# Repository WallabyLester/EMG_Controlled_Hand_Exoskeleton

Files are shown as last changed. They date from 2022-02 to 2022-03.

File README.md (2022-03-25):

# EMG Controlled Hand Exoskeleton

https://user-images.githubusercontent.com/90433630/159782526-b3bb951d-2681-48af-9a75-46fd34234eaf.mp4
<p>Playing You Are My Sunshine</p>

## Overview
The goal of this project was to design an EMG controlled hand exoskeleton that would aid stroke patients in playing the piano. The exoskeleton is 3D printed with the `.stl` and `.step` files located in the `cad` directory. You can view individual `.stl` files to see what the parts look like prior to printing. Parts were printed on a Ultimaker 3 with black tough PLA. Most connections are press fit or printed, but four screws and nuts are needed to connect the metacarpal to the hand_dorsal (washers can be added if the screw/nut pair is not big enough). Refer to `cad/exoskeleton.png` for an image of what the completed exoskeleton looks like. 

Four Pololu HP 6V 298:1 Micro Metal Gearmotors were used for the joints and are housed in the finger joint. 12 CPR, 2.7-18V Magnetic Encoders from Pololu were used for each motor. MyoWare Muscle Sensors were used to acquire the EMG signals. 

The microcontroller for this project was an Arduino Uno; used for speed of prototyping, but can be upgraded to any controller if equivalent motor drivers are added. The motor driver in this case was the Adafruit Motor Shield as it allowed direct interfacing with the Arduino and control of four DC motors. 

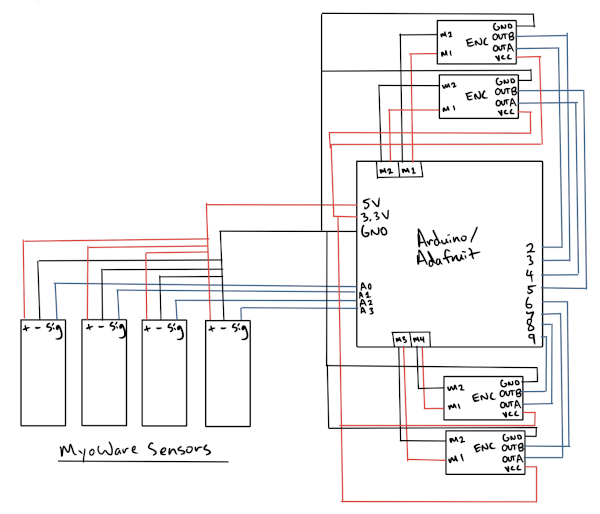
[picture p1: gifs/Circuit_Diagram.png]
Circuit Diagram


There are three available control modes:
1. Using thresholds. Thresholding uses manually found thresholds from EMG readings and basic motor control in which the fingers move up and down a set amount based on an input power. 

2. Using machine learning (ML) classification. ML classification uses the contained ML models to predict which finger is being moved and moves the associated motor with basic motor control based on an input power.

3. Using ML classification with encoder position control from a PID feedback loop. ML classification with the encoders implements external and internal interrupts to read encoder values and perform position control using a PID feedback loop. The Arduino Uno only has two interrupt pins (2 and 3) so an internal interrupt was made using Timer1 (16 bit). 

The control signal is provided by Myoware EMG sensors which provide a processed EMG signal. The signals are amplified, rectified, and integrated before being output. The sensors also offer a raw EMG signal if you would like to perform your own processing. Code for reading from the EMG sensors, saving readings, and plotting data are in the `code` directory. 

Machine learning is used on the EMG readings received from four sensor readings, enabling classification of the signals in 5 modes: 0 - no flexion, 1 - index finger flexed, 2 - middle finger flexed, 3 - fourth finger flexed, and 4 - pinky finger flexed. `Classification_Notes` contains the various scikit-learn machine learning models as well as a Tensorflow model. Refer to it for further notes on the models and GridSearchCV to find the best hyperparameters for the models. The trained models have been saved serialized in the `Trained_models` directory.

There are four available models: 

1. K Nearest Neighbors - KNN predicts the class by calculating the distance between the input point and all of the other points. The algorithm then selects the K number of points which is closest to the input point and uses a majority vote for which class this input must be in. 

2. Random forest classifier - RFC is made up of many decision trees. It builds an uncorrelated forest of trees which can provide a more accurate prediction than just one tree. Decision trees predict an input class based on decision rules which causes branches from each "node". 

3. Multilayer perceptron - MLP is a feed forward neural network. It uses an input layer, output layer, and any number of hidden layers. With an increased number of hidden layers it is able to predict more complex classes. They can also solved non-linear classification problems.

## Usage Instructions
Compile `EMGControlEncoder.ino` onto the Arduino and run `Send_Mode.py` in a terminal with `python3 Send_Mode.py` to start predicting EMG readings. The code will print out the predicted mode. 

Use `EMGControl.ino` for running ML classification with basic motor control and `EMGControlThresholds.ino` to run basic motor control using thresholds. 

Use `EMGControlTest.ino` if you would like to test individual EMG sensor and motor control.

Use `EMGToSerial.ino` to output the EMG readings as serial data and run `Read_EMG_Data.py` to save the data. Run `Plotting.py` to plot individual data file EMG readings and modes.

Use `EncoderRead.ino` to read all the encoders and `EncoderPosition.ino` to control motor movements using all the encoders. 

Use `MotorControl.ino` to test movement of individual motors and `Stop.ino` to stop all motor movement if you are running things and would like to halt them.

## Configuration Instructions
The classification model used in `Send_Mode.py` can be changed based on which ML model you would like to use. Change the line: `filename` to use different models.

The encoder positions can be adjusted based on the desired amount to move the fingers. These would be the `pos_index`, `pos_middle`, `pos_fourth`, and `pos_pinky` variables in the encoder control files.

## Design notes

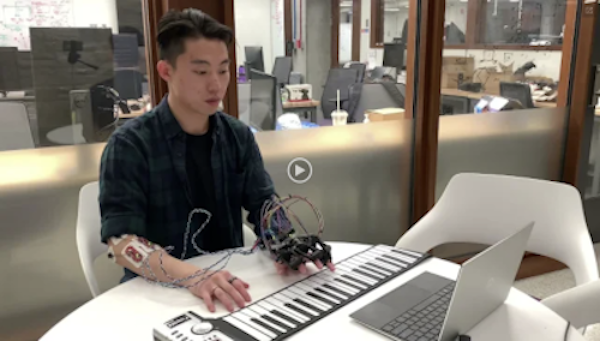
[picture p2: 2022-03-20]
gifs/Final_Demo.png

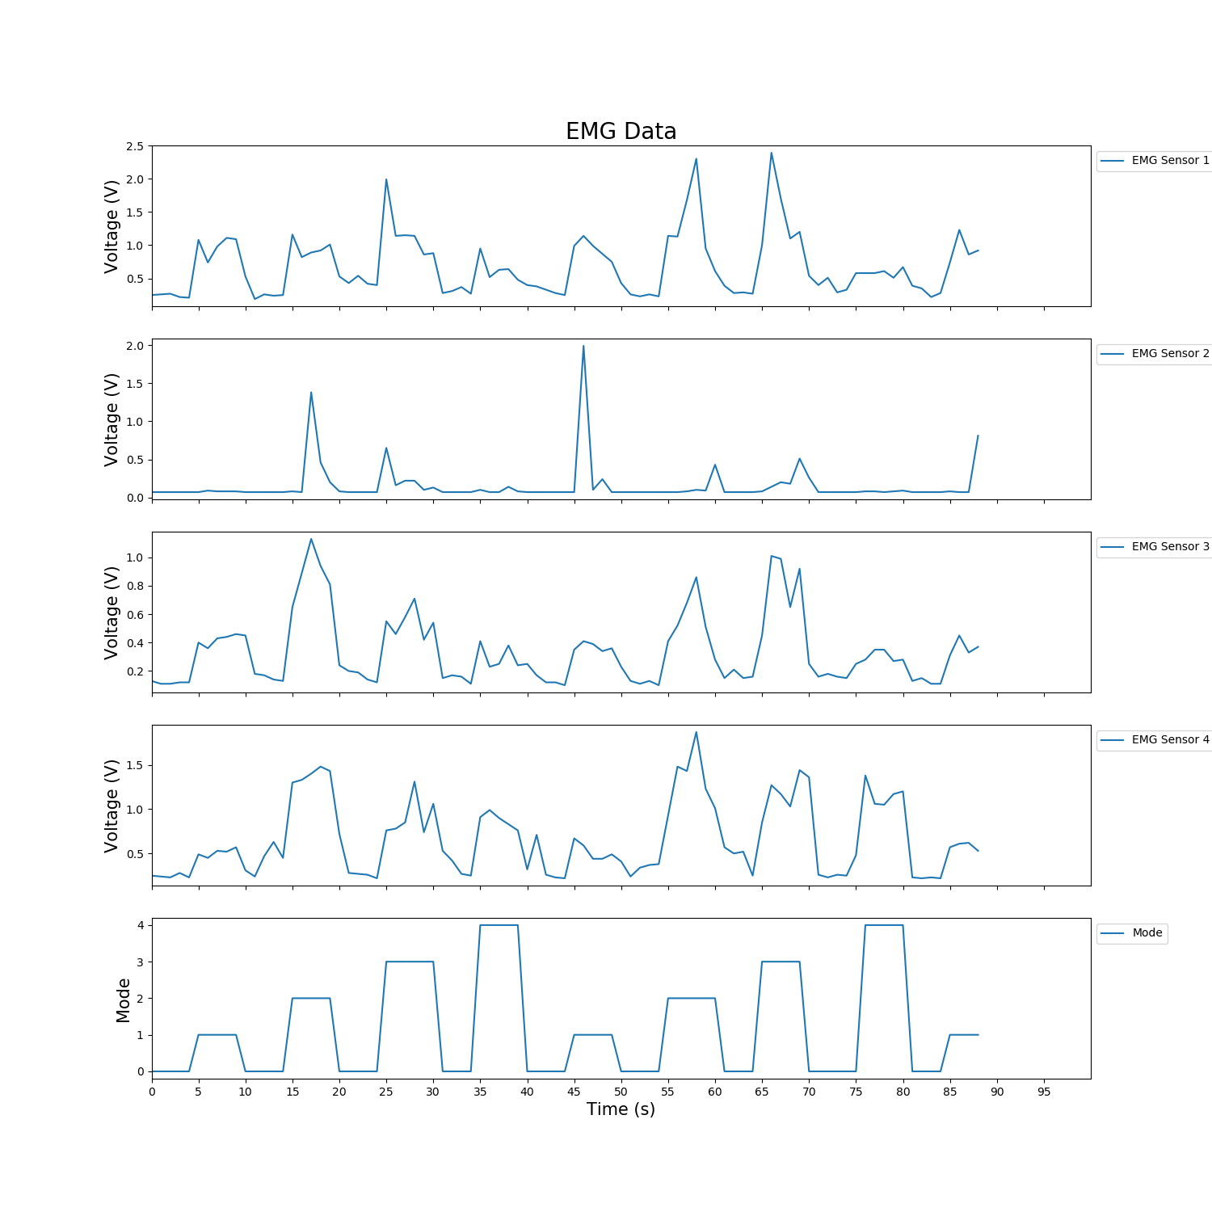
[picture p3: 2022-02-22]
code/plots/Combined_EMG_data5.png

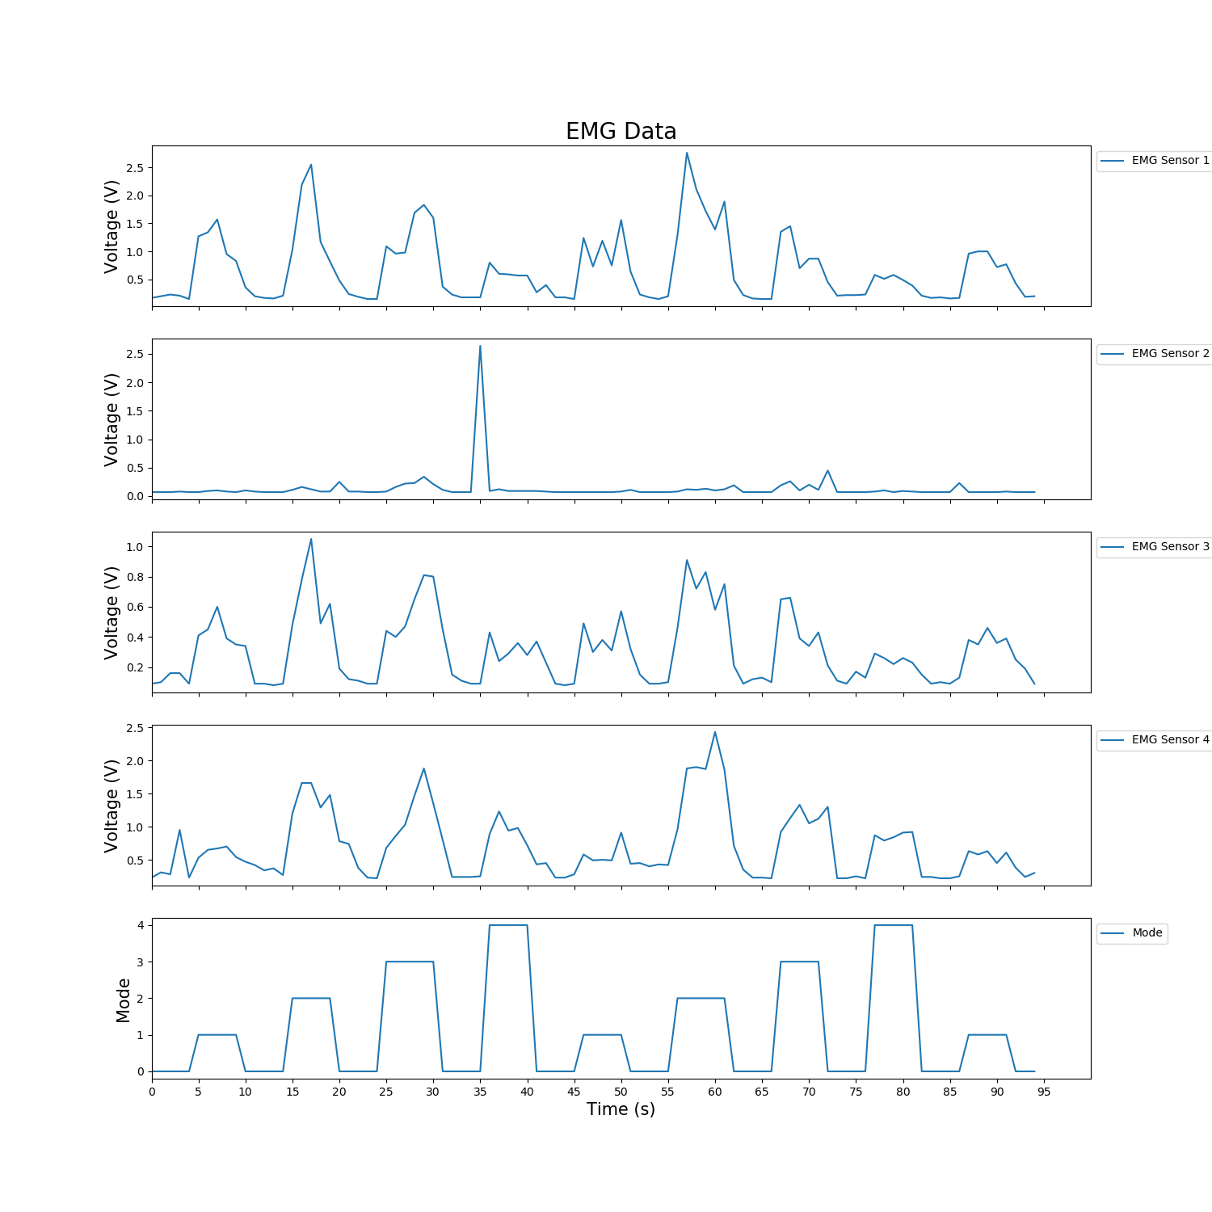
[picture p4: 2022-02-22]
code/plots/Combined_EMG_data8.png

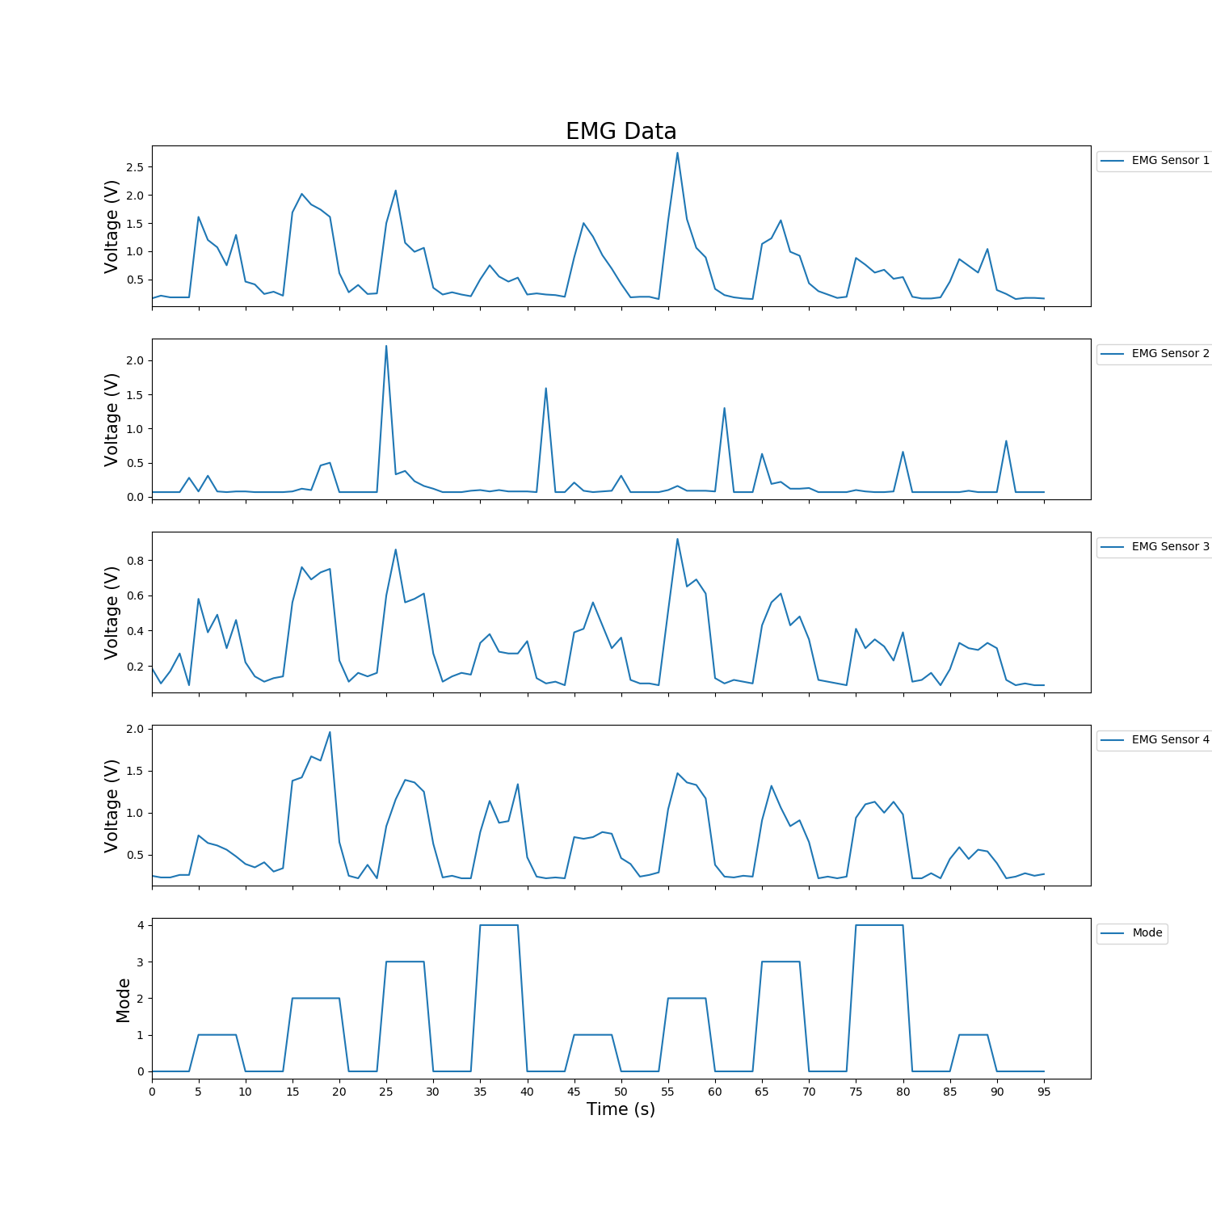
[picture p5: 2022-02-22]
code/plots/Combined_EMG_data10.png

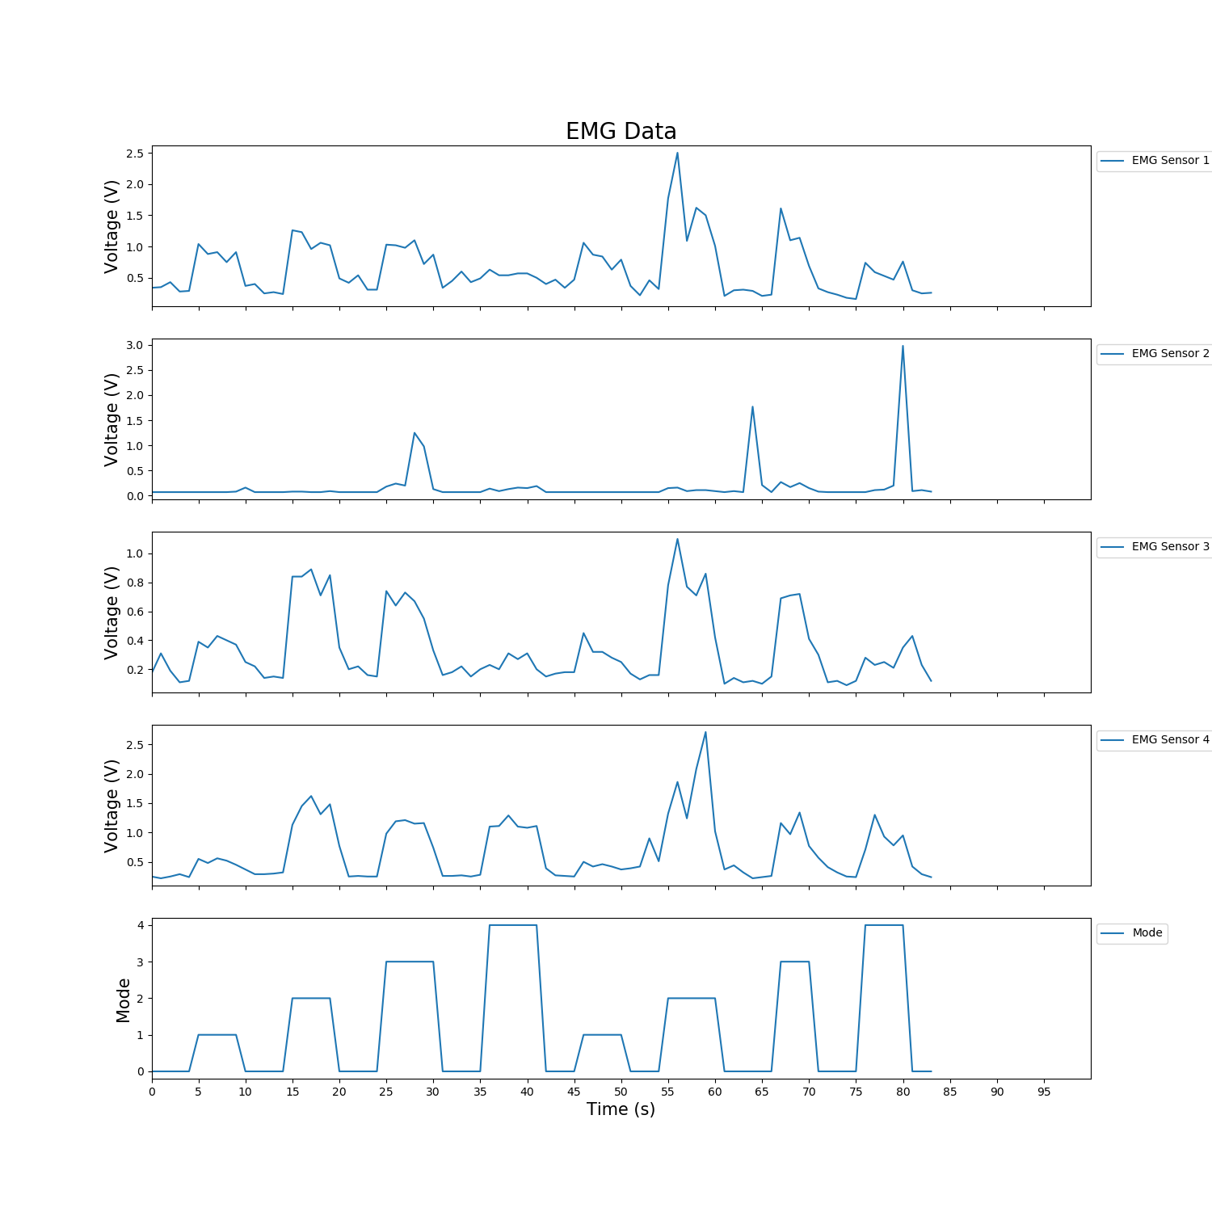
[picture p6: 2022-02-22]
code/plots/Combined_EMG_data3.png

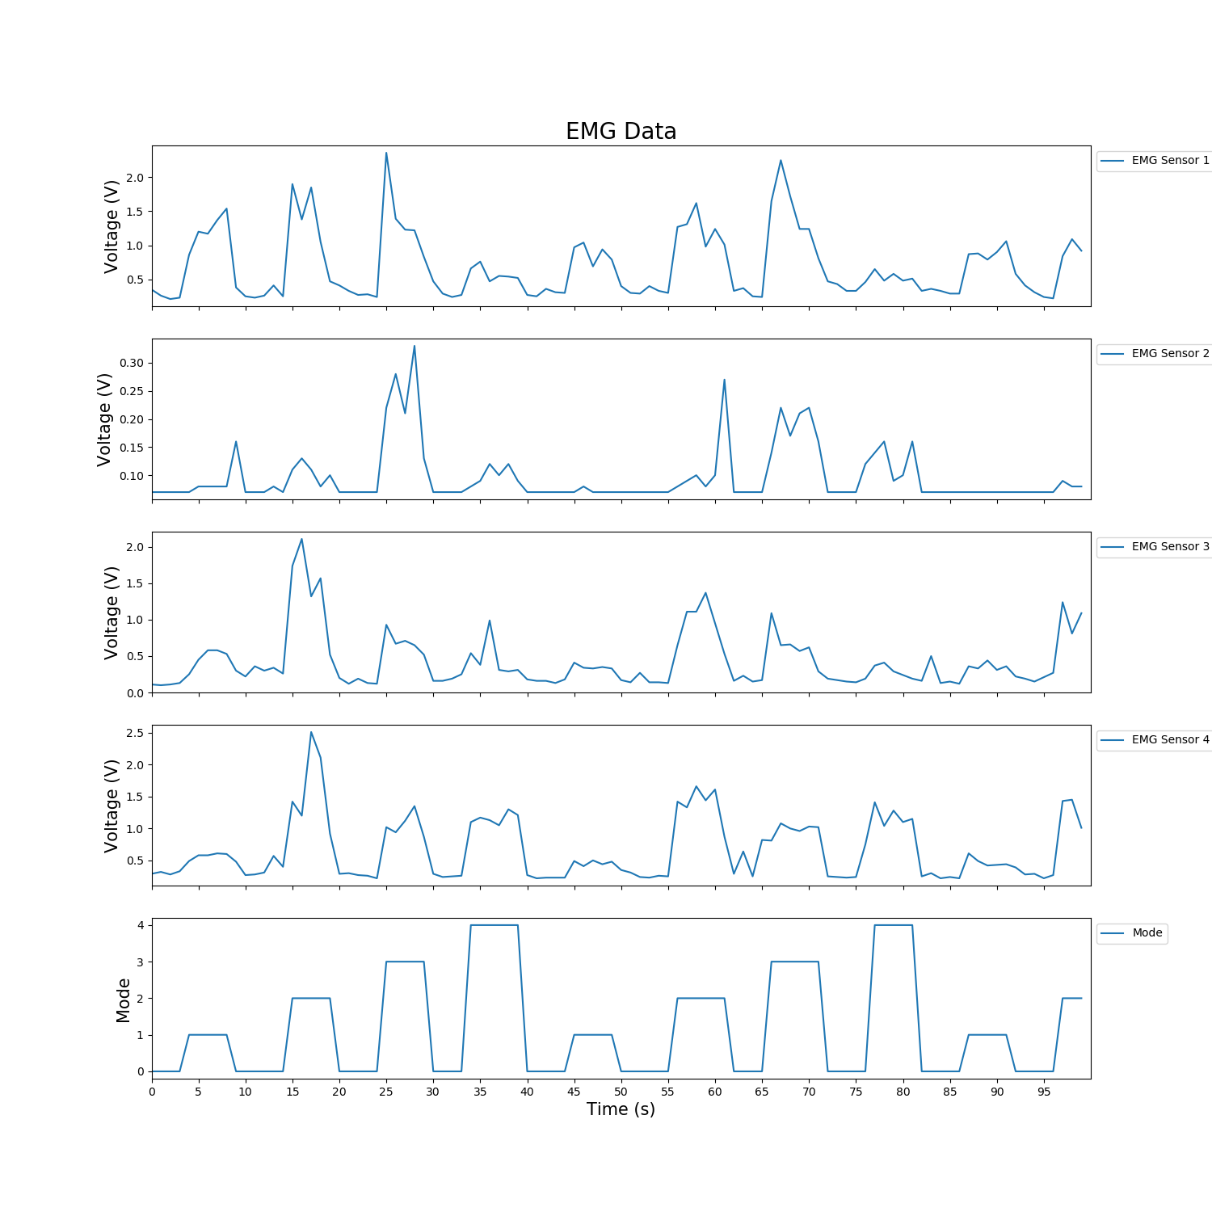
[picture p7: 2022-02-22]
code/plots/Combined_EMG_data1.png

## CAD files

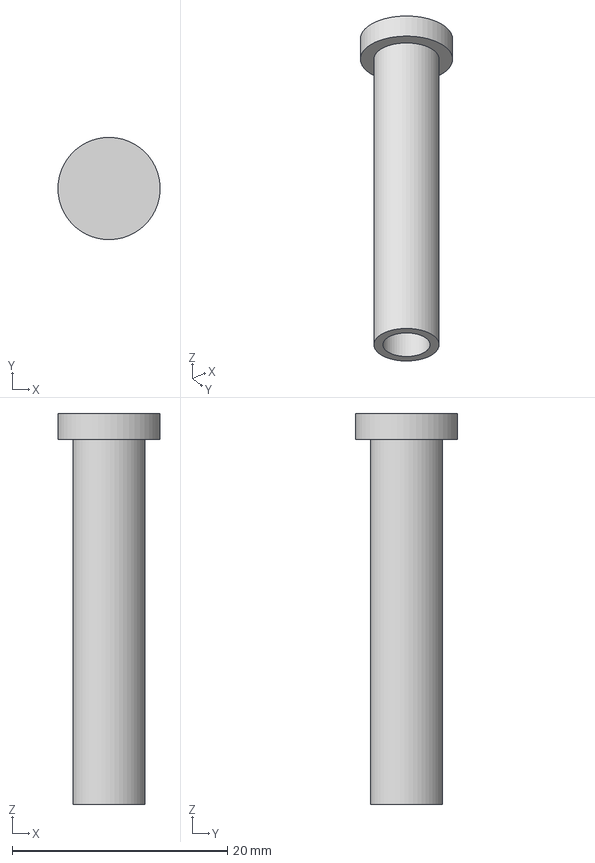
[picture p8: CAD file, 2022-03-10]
cad/Fingertip_Pin.stp
9.49 x 9.49 x 36.3 mm

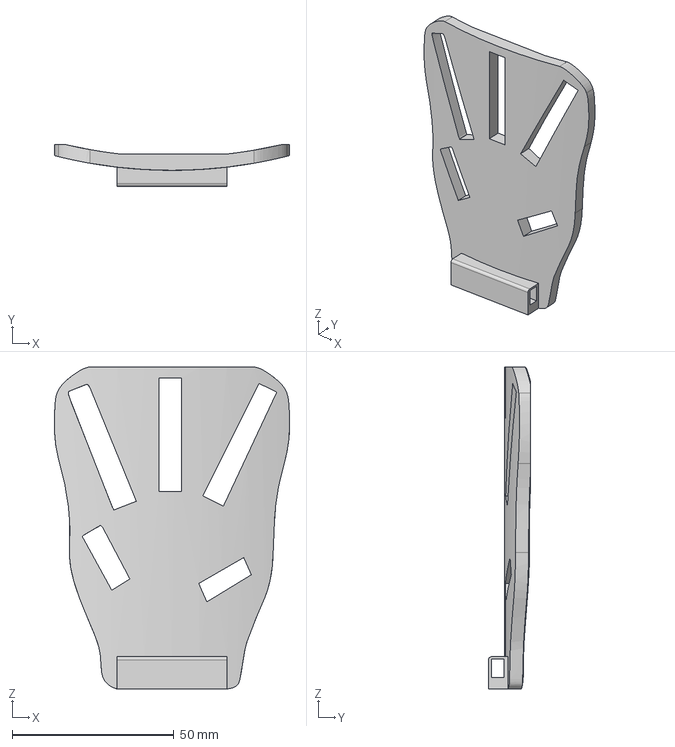
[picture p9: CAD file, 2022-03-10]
cad/Hand_Dorsal.stp
72.7 x 13.0 x 99.5 mm

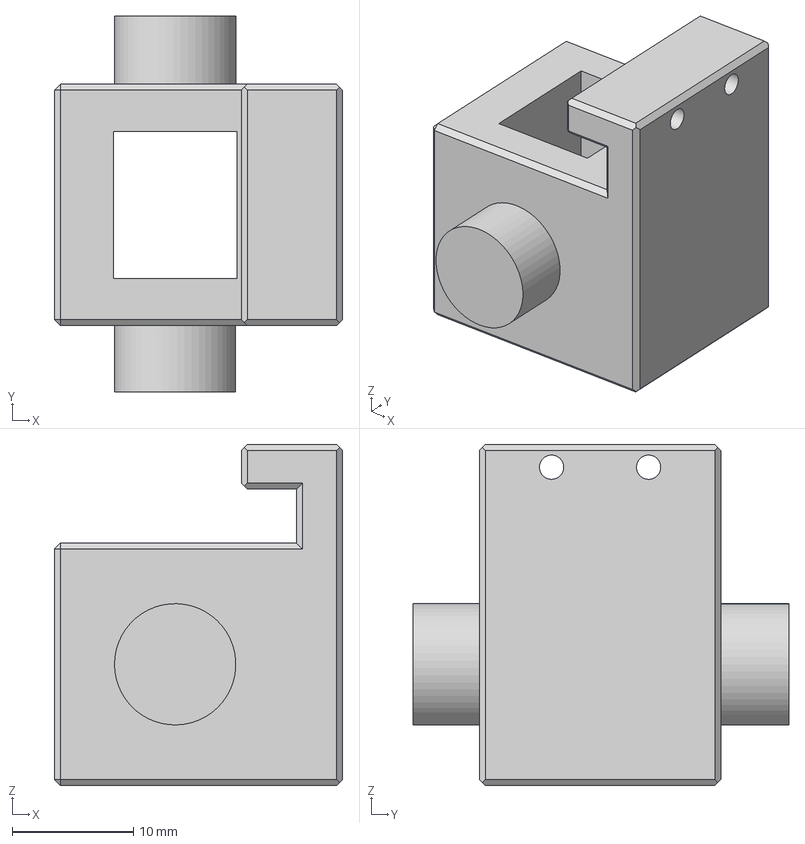
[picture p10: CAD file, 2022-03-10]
cad/Finger_Joint.stp
23.8 x 31.0 x 28.1 mm

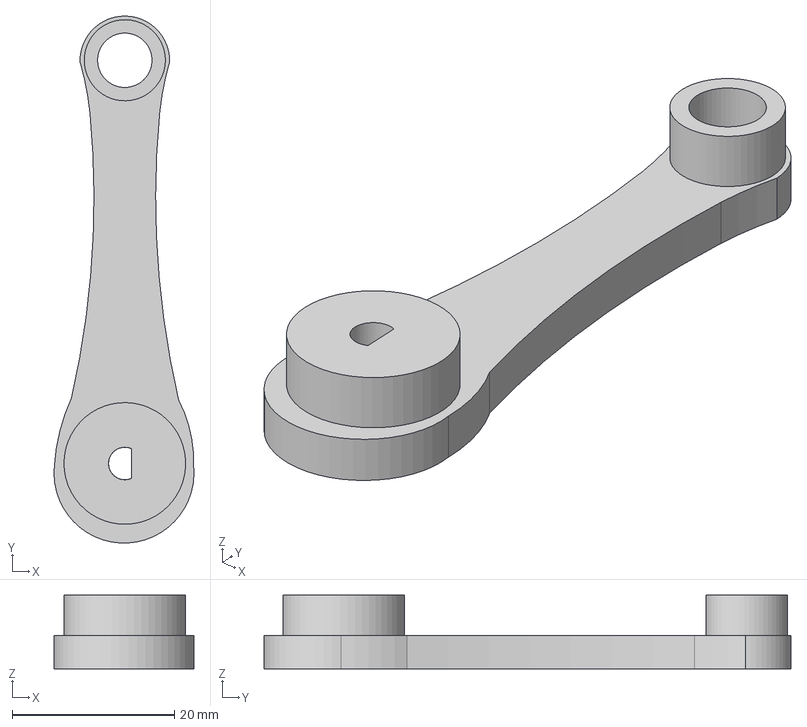
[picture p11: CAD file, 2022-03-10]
cad/Finger_Side_Two.stp
17.3 x 65.0 x 9.10 mm

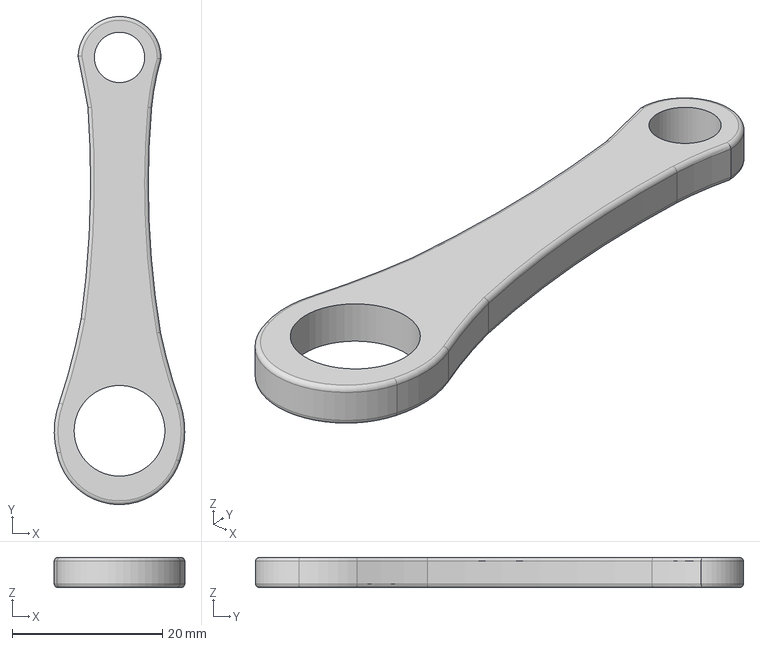
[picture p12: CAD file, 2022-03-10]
cad/Finger_Side_One.stp
17.4 x 65.0 x 4.00 mm

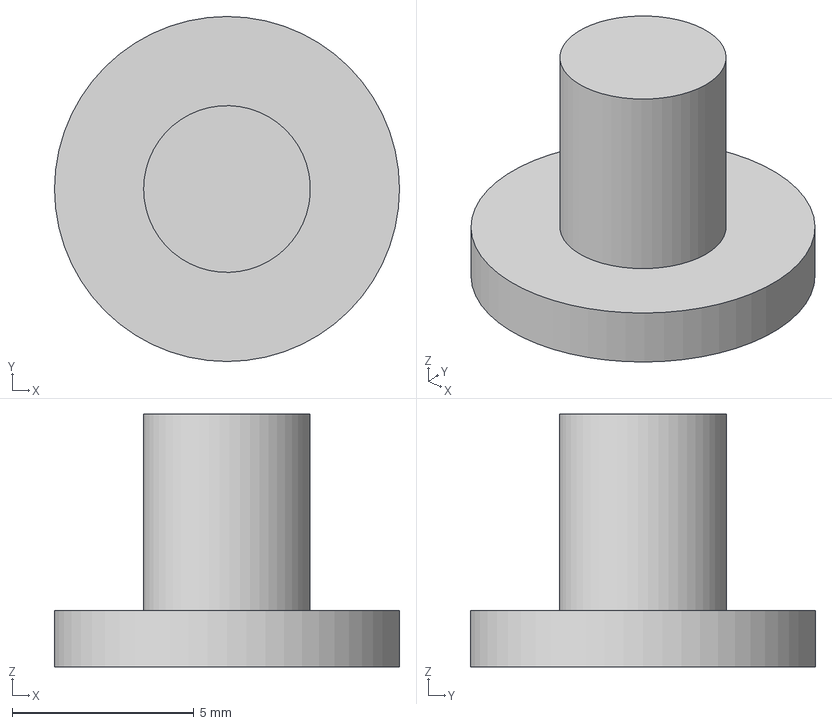
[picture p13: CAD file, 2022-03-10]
cad/Fingertip_Cap.stp
9.50 x 9.50 x 6.97 mm

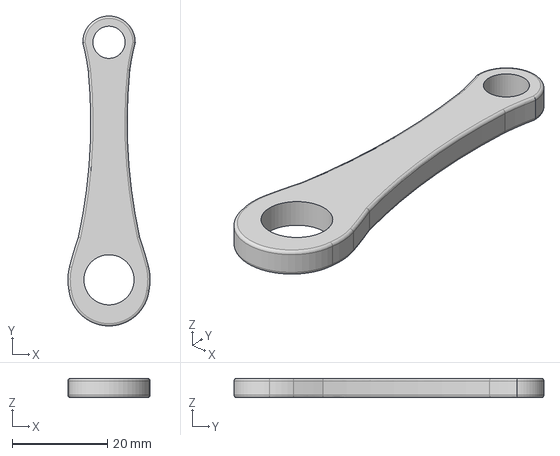
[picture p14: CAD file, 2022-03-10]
cad/Metacarpal.stp
17.3 x 65.0 x 4.00 mm

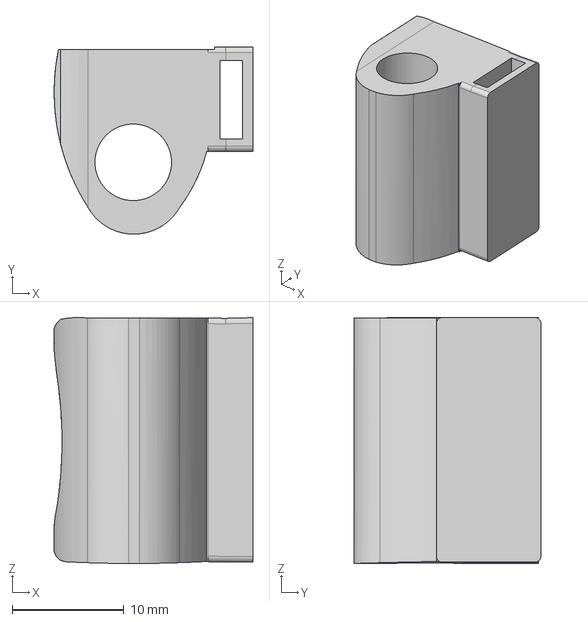
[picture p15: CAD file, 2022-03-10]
cad/Fingertip.stp
17.8 x 16.7 x 22.0 mm

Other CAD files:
cad/Finger_Joint.stl
cad/Finger_Side_One.stl
cad/Finger_Side_Two.stl
cad/Fingertip.stl
cad/Fingertip_Cap.stl
cad/Fingertip_Pin.stl
cad/Hand_Dorsal.stl
cad/Metacarpal.stl

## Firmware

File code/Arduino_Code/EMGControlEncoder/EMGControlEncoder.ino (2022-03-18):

/********************************************************************
 * Read analog input of Myoware EMG sensor and convert it to voltage 
 * to control motor using encoders.
 * 
 * Implements external and internal interrupts to read encoders PID
 * feedback control loop.
 ********************************************************************/

#include <Wire.h>
#include <Adafruit_MotorShield.h>
#include "utility/Adafruit_MS_PWMServoDriver.h"

// Initialize motor driver and each motor
Adafruit_MotorShield AFMS = Adafruit_MotorShield();
Adafruit_DCMotor *myMotor1 = AFMS.getMotor(1);
Adafruit_DCMotor *myMotor2 = AFMS.getMotor(2);
Adafruit_DCMotor *myMotor3 = AFMS.getMotor(3);
Adafruit_DCMotor *myMotor4 = AFMS.getMotor(4);

// Define encoder channel pins
#define ENCA_index 2    // Only pins 2 and 3 are interrupt pins on Arduino Uno
#define ENCB_index 3
#define ENCA_middle 4  
#define ENCB_middle 5
#define ENCA_fourth 7  
#define ENCB_fourth 6
#define ENCA_pinky 8  
#define ENCB_pinky 9 

// Initialize encoder position counters
int pos_index = 0;
int pos_middle = 0;
int pos_fourth = 0;
int pos_pinky = 0; 

// Initialize encoder channel readings
int a_middle_prev = 0;
int a_middle = 0;
int b_middle_prev = 0;
int b_middle = 0;

int a_fourth_prev = 0;
int a_fourth = 0;
int b_fourth_prev = 0;
int b_fourth = 0;

int a_pinky_prev = 0;
int a_pinky = 0;
int b_pinky_prev = 0;
int b_pinky = 0;

// Define sensor pins and initialize values
int sensor1Pin = A0;
int sensor2Pin = A1;
int sensor3Pin = A2;
int sensor4Pin = A3;

int sensorVal1 = 0;
int sensorVal2 = 0;
int sensorVal3 = 0;
int sensorVal4 = 0;

int freq = 1000; 
int incomingByte = 0;

// Constants for feedback control loop
int target = 0, dir = 0;
long prevT = 0;
float eprev = 0, eintegral = 0, pwr = 0;

// Function prototypes
void bend(Adafruit_DCMotor* motor, int _dir, float power);
void stop();
void PID(int pos, int goal);

void setup() 
{
    // Initialize serial communication at 9600 bits per second
    Serial.begin(9600);
    AFMS.begin();

    // Set encoder pins as inputs to read channels
    pinMode(ENCA_index, INPUT);
    pinMode(ENCB_index, INPUT);
    pinMode(ENCA_middle, INPUT);
    pinMode(ENCB_middle, INPUT);
    pinMode(ENCA_fourth, INPUT);
    pinMode(ENCB_fourth, INPUT);
    pinMode(ENCA_pinky, INPUT);
    pinMode(ENCB_pinky, INPUT);

    // Initialize Arduino Timer 1: 16 bit timer
    cli();
    TCCR2A = 0b01010011;
    TCCR2B = 0b00001100;
    OCR2A = 84;
    OCR2B = OCR2A/2; 
    TIMSK1 |= B00000010;
    sei();

    // Using built in interrupt pins for index finger
    attachInterrupt(digitalPinToInterrupt(ENCA_index), readIndexEncoder, RISING);
}

void loop() 
{
    sensorVal1 = analogRead(sensor1Pin);            // read the input on analog pin
    float voltage1 = sensorVal1 * (5.0 / 1023.0);   // Convert the analog reading to a voltage

    sensorVal2 = analogRead(sensor2Pin);           
    float voltage2 = sensorVal2 * (5.0 / 1023.0);

    sensorVal3 = analogRead(sensor3Pin);           
    float voltage3 = sensorVal3 * (5.0 / 1023.0);

    sensorVal4 = analogRead(sensor4Pin);           
    float voltage4 = sensorVal4 * (5.0 / 1023.0); 

    // Output readings in serial buffer
    Serial.print(voltage1);
    Serial.print(",");
    Serial.print(voltage2);
    Serial.print(",");
    Serial.print(voltage3);
    Serial.print(",");
    Serial.println(voltage4);

    delay(freq); 

    // Read encoder channels for current state
    a_middle_prev = digitalRead(ENCA_middle);
    b_middle_prev = digitalRead(ENCB_middle);

    a_fourth_prev = digitalRead(ENCA_fourth);
    b_fourth_prev = digitalRead(ENCA_fourth);

    a_pinky_prev = digitalRead(ENCA_pinky);
    b_pinky_prev = digitalRead(ENCA_pinky);

    if (Serial.available() > 0) 
    {
        // read the oldest byte in the serial buffer
        incomingByte = Serial.read();

        if (incomingByte == '0') 
        {
            // Classified as no flexion, will return fingers to starting positions
            // Works ideally with index finger; however, encoder resolution is an
            // issue with timer run encoders
            // PID(pos_index, 0);
            // bend(myMotor1, dir, pwr);
            // PID(pos_middle, 0);
            // bend(myMotor2, dir, pwr);
            // PID(pos_fourth, 0);
            // bend(myMotor3, dir, pwr);
            // PID(pos_pinky, 0);
            // bend(myMotor4, dir, pwr);
        }
    
        if (incomingByte == '1') 
        {
            // Classified as index finger, sends desired encoder positions to press down and lift
            PID(pos_index, -500);
            bend(myMotor1, dir, pwr);
            PID(pos_index, 200);
            bend(myMotor1, dir, pwr);
        }

        if (incomingByte == '2') 
        {
            // Classified as middle finger
            PID(pos_middle, -400);
            bend(myMotor2, dir, pwr);
            PID(pos_middle, 200);
            bend(myMotor2, dir, pwr);
        }

        if (incomingByte == '3') 
        {
            // Classified as fourth finger
            PID(pos_fourth, -400);
            bend(myMotor3, dir, pwr);
            PID(pos_fourth, 200);
            bend(myMotor3, dir, pwr);
        }

        if (incomingByte == '4') 
        {
            // Classified as pinky finger
            PID(pos_pinky, -400);
            bend(myMotor4, dir, pwr);
            PID(pos_pinky, 200);
            bend(myMotor4, dir, pwr);
        }
    }
}

// Function to move desired motor based on PID control
// Params :
//      motor - Desired motor number
//      _dir - direction to move
//      power - power to give motor between 0 and 255
void bend(Adafruit_DCMotor* motor, int _dir, float power)
{
    motor->setSpeed(power);

    if (_dir == 1)                      // Move CW
    {
        motor->run(FORWARD);
        delay(freq);
        motor->run(RELEASE);
        delay(freq);
    }
    else if (_dir == -1)                // Move CCW
    {
        motor->run(BACKWARD);
        delay(freq);
        motor->run(RELEASE);
        delay(freq);
    }
    else                                // Don't move
    {
        myMotor1->run(RELEASE);
        myMotor2->run(RELEASE);
        myMotor3->run(RELEASE);
        myMotor4->run(RELEASE);
    }
}

// Function to stop the motors from moving
void stop()
{
    myMotor1->run(RELEASE);
    myMotor2->run(RELEASE);
    myMotor3->run(RELEASE);
    myMotor4->run(RELEASE);
}

// Function to implement PID position feedback control
// Params :
//      pos - current position
//      goal - desired position
void PID(int pos, int goal)
{
    // Define proportional, integral, and derivative gains
    float kp = 0.1;
    float ki = 0;
    float kd = 0.1;

    // Set time difference 
    long currT = micros();

    float deltaT = ((float)(currT-prevT))/1.0e6;
    prevT = currT;

    // Error between current position and goal
    int e = pos-goal; 

    // Compute derivative 
    float dedt = (e-eprev)/(deltaT);

    // Compute integral 
    eintegral = eintegral + e*deltaT;

    // Compute control signal
    float u = kp*e + kd*dedt + ki*eintegral;

    // Use absolute value for the motor power
    pwr = fabs(u);

    // Motor direction clockwise unless control signal is negative
    dir = 1;

    if (u<0)
    {
        dir = -1;
    }

    // Store previous error
    eprev = e;
}

// ISR for index finger encoder
void readIndexEncoder()
{
    int b_index = digitalRead(ENCB_index);
    if(b_index>0)
    {
        pos_index++;  // CW (finger up)
    }
    else
    {
        pos_index--;  // CCW (finger down)
    }
}

// ISR for Timer1
// Reads encoders for middle, fourth, and pinky fingers
ISR(TIMER1_COMPA_vect)    
{  
    // Read middle finger channel A 
    a_middle = digitalRead(ENCA_middle);

    // RISING edge: from LOW to HIGH
    if (a_middle_prev == LOW && a_middle == HIGH)
    {
        // Read middle finger channel B 
        b_middle = digitalRead(ENCB_middle);

        // Encoder lookup table for CW and CCW
        if(a_middle_prev == LOW && b_middle_prev == LOW && a_middle == LOW && b_middle == HIGH)
        {
            pos_middle--; 
        }
        else if (a_middle_prev == LOW && b_middle_prev == LOW && a_middle == HIGH && b_middle == LOW)
        {
            pos_middle++;
        }
        else if (a_middle_prev == LOW && b_middle_prev == HIGH && a_middle == HIGH && b_middle == HIGH)
        {
            pos_middle--; 
        }
        else if (a_middle_prev == LOW && b_middle_prev == HIGH && a_middle == LOW && b_middle == LOW)
        {
            pos_middle++; 
        }
        else if (a_middle_prev == HIGH && b_middle_prev == LOW && a_middle == LOW && b_middle == LOW)
        {
            pos_middle--; 
        }
        else if (a_middle_prev == HIGH && b_middle_prev == LOW && a_middle == HIGH && b_middle == HIGH)
        {
            pos_middle++; 
        }
        else if (a_middle_prev == HIGH && b_middle_prev == HIGH && a_middle == HIGH && b_middle == LOW)
        {
            pos_middle--; 
        }
        else if (a_middle_prev == HIGH && b_middle_prev == HIGH && a_middle == LOW && b_middle == HIGH)
        {
            pos_middle++; 
        }
    }
    // Save current readings as previous
    a_middle_prev = a_middle;
    b_middle_prev = b_middle;

    // Read fourth finger channel A
    a_fourth = digitalRead(ENCA_fourth);

    // RISING edge: from LOW to HIGH
    if (a_fourth_prev == LOW && a_fourth == HIGH)
    {
        // Read fourth finger channel B 
        b_fourth = digitalRead(ENCB_fourth);

        // Encoder lookup table for CW and CCW
        if(a_fourth_prev == LOW && b_middle_prev == LOW && a_fourth == LOW && b_fourth == HIGH)
        {
            pos_fourth--; 
        }
        else if (a_fourth_prev == LOW && b_middle_prev == LOW && a_fourth == HIGH && b_fourth == LOW)
        {
            pos_fourth++;
        }
        else if (a_fourth_prev == LOW && b_middle_prev == HIGH && a_fourth == HIGH && b_fourth == HIGH)
        {
            pos_fourth--; 
        }
        else if (a_fourth_prev == LOW && b_middle_prev == HIGH && a_fourth == LOW && b_fourth == LOW)
        {
            pos_fourth++; 
        }
        else if (a_fourth_prev == HIGH && b_middle_prev == LOW && a_fourth == LOW && b_fourth == LOW)
        {
            pos_fourth--; 
        }
        else if (a_fourth_prev == HIGH && b_middle_prev == LOW && a_fourth == HIGH && b_fourth == HIGH)
        {
            pos_fourth++; 
        }
        else if (a_fourth_prev == HIGH && b_middle_prev == HIGH && a_fourth == HIGH && b_fourth == LOW)
        {
            pos_fourth--; 
        }
        else if (a_fourth_prev == HIGH && b_middle_prev == HIGH && a_fourth == LOW && b_fourth == HIGH)
        {
            pos_fourth++; 
        }
    }
    // Save current readings as previous
    a_fourth_prev = a_fourth;
    b_fourth_prev = b_fourth;

    // Read pinky finger channel A
    a_pinky = digitalRead(ENCA_pinky);

    // RISING edge: from LOW to HIGH
    if (a_pinky_prev == LOW && a_pinky == HIGH)
    {
        // Read fourth finger channel B 
        b_pinky = digitalRead(ENCB_pinky);
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

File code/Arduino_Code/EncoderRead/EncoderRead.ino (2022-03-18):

#define ENCA_index 2  // purple
#define ENCB_index 3  // blue
#define ENCA_middle 4  // purple
#define ENCB_middle 5  // blue
#define ENCA_fourth 7  // purple
#define ENCB_fourth 6  // blue
#define ENCA_pinky 8  // purple
#define ENCB_pinky 9  // blue

int pos_index = 0;
int pos_middle = 0;
int pos_fourth = 0;
int pos_pinky = 0; 

int a_middle_prev = 0;
int a_middle = 0;
int b_middle_prev = 0;
int b_middle = 0;

int a_fourth_prev = 0;
int a_fourth = 0;
int b_fourth_prev = 0;
int b_fourth = 0;

int a_pinky_prev = 0;
int a_pinky = 0;
int b_pinky_prev = 0;
int b_pinky = 0;

void setup()
{
    Serial.begin(9600);
    
    pinMode(ENCA_index, INPUT);
    pinMode(ENCB_index, INPUT);
    pinMode(ENCA_middle, INPUT);
    pinMode(ENCB_middle, INPUT);
    pinMode(ENCA_fourth, INPUT);
    pinMode(ENCB_fourth, INPUT);
    pinMode(ENCA_pinky, INPUT);
    pinMode(ENCB_pinky, INPUT);

    cli();
    TCCR2A = 0b01010011;
    TCCR2B = 0b00001100;
    OCR2A = 84;
    OCR2B = OCR2A/2; 
    TIMSK1 |= B00000010;
    sei();

    attachInterrupt(digitalPinToInterrupt(ENCA_index), readIndexEncoder, RISING);
}

void loop()
{
    a_middle_prev = digitalRead(ENCA_middle);
    b_middle_prev = digitalRead(ENCB_middle);

    a_fourth_prev = digitalRead(ENCA_fourth);
    b_fourth_prev = digitalRead(ENCA_fourth);

    a_pinky_prev = digitalRead(ENCA_pinky);
    b_pinky_prev = digitalRead(ENCA_pinky);

    Serial.print(pos_index); 
    Serial.print(" ");
    Serial.print(pos_middle);
    Serial.print(" ");
    Serial.print(pos_fourth);
    Serial.print(" ");
    Serial.print(pos_pinky);
    Serial.println();
}

void readIndexEncoder()
{
    int b_index = digitalRead(ENCB_index);
    if(b_index>0)
    {
        pos_index++;  //CW (up)
    }
    else
    {
        pos_index--;  //CCW (down)
    }
}

ISR(TIMER1_COMPA_vect)    
{  
    // middle finger
    a_middle = digitalRead(ENCA_middle);

    // RISING: from LOW to HIGH
    if (a_middle_prev == LOW && a_middle == HIGH)
    {
      b_middle = digitalRead(ENCB_middle);

      if(a_middle_prev == LOW && b_middle_prev == LOW && a_middle == LOW && b_middle == HIGH)
      {
          pos_middle--; 
      }
      else if (a_middle_prev == LOW && b_middle_prev == LOW && a_middle == HIGH && b_middle == LOW)
      {
          pos_middle++;
      }
      else if (a_middle_prev == LOW && b_middle_prev == HIGH && a_middle == HIGH && b_middle == HIGH)
      {
          pos_middle--; 
      }
      else if (a_middle_prev == LOW && b_middle_prev == HIGH && a_middle == LOW && b_middle == LOW)
      {
          pos_middle++; 
      }
      else if (a_middle_prev == HIGH && b_middle_prev == LOW && a_middle == LOW && b_middle == LOW)
      {
          pos_middle--; 
      }
      else if (a_middle_prev == HIGH && b_middle_prev == LOW && a_middle == HIGH && b_middle == HIGH)
      {
          pos_middle++; 
      }
      else if (a_middle_prev == HIGH && b_middle_prev == HIGH && a_middle == HIGH && b_middle == LOW)
      {
          pos_middle--; 
      }
      else if (a_middle_prev == HIGH && b_middle_prev == HIGH && a_middle == LOW && b_middle == HIGH)
      {
          pos_middle++; 
      }
    }
    a_middle_prev = a_middle;
    b_middle_prev = b_middle;

    // fourth finger
    a_fourth = digitalRead(ENCA_fourth);

    // RISING: from LOW to HIGH
    if (a_fourth_prev == LOW && a_fourth == HIGH)
    {
      b_fourth = digitalRead(ENCB_fourth);
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

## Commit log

2022-02-01 Push of arduino, data recording, and plotting code
    [EMG_data1.csv, EMG_data2.csv, EMG_data3.csv, EMG_data4.csv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]
2022-02-17 Pushing cad files and EMG arduino and python code
    [Back_Hand_Left_Hand_Desk.stl, Combined_EMG_data1.csv, Finger_Motor_Joint_Desk.stl, Finger_Motor_Panel_Front_Desk.stl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]
2022-02-20 Updated plotting code for four sensors
    [Combined_EMG_data1.csv]
2022-02-20 Recorded 10 emg data samples
    [Combined_EMG_data1.csv, Combined_EMG_data10.csv, Combined_EMG_data2.csv, Combined_EMG_data3.csv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]
2022-02-22 10 data sets and plots, version 2 of hand control sketch
    [Combined_EMG_data1.csv, Combined_EMG_data10.csv, Combined_EMG_data2.csv, Combined_EMG_data3.csv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]
2022-03-10 Recorded additional data and added more model options
    [Combined_EMG_data11.csv, Combined_EMG_data12.csv, Combined_EMG_data13.csv, Combined_EMG_data14.csv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]
2022-03-10 Cleaned up files and added final cad design
    [Finger_Joint.stl, Finger_Joint.stp, Finger_Side_One.stl, Finger_Side_One.stp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]
2022-03-14 Addition of encoder reading and control code
    [Combined_EMG_data31.csv, Combined_EMG_data32.csv, Combined_EMG_data33.csv, Combined_EMG_data34.csv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]
2022-03-18 Completed documentation for all arduino code
    [EMG_data1.csv, EMG_data2.csv, EMG_data3.csv, EMG_data4.csv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]
2022-03-21 Adding circuit diagram
